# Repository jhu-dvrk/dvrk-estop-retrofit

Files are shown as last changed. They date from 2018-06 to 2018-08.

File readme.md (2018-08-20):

# dVRK E-stop Retrofit Kit

This retrofit kit converts the 4-pin and 5-pin E-stop connectors on old dVRK boxes to the newer 4-and-5-pin connectors.

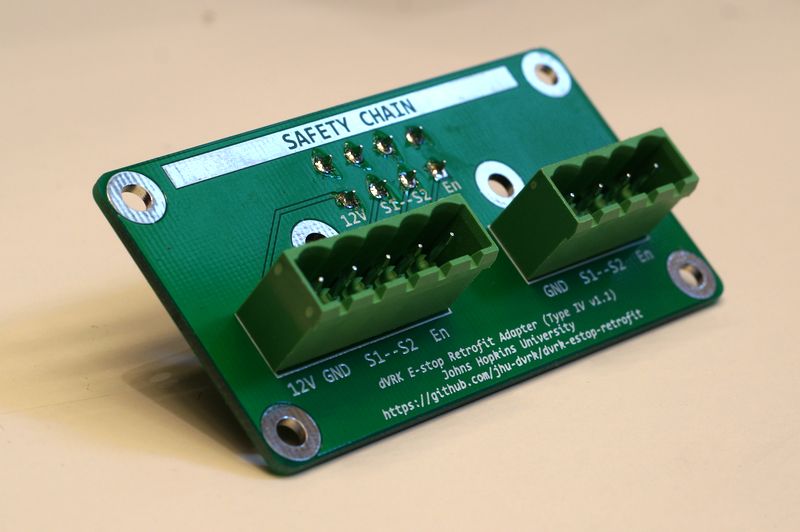
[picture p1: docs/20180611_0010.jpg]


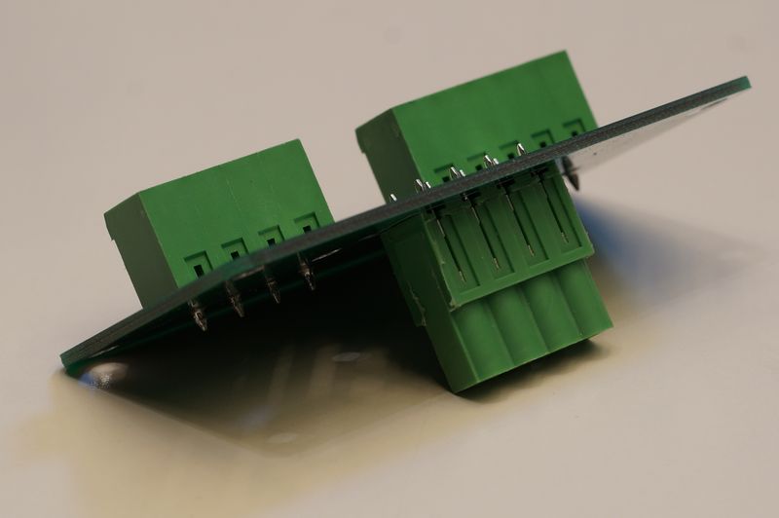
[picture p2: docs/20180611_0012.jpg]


**Why do I want the new 4-and-5-pin connectors?** The new connectors allow you to use the [JHU-style configurable serial connection](#making-the-cables), so you can quickly reconfigure the dVRK into two or more systems (e.g. one workstation for the MTMs, and another workstation for the PSMs) for different research needs. 

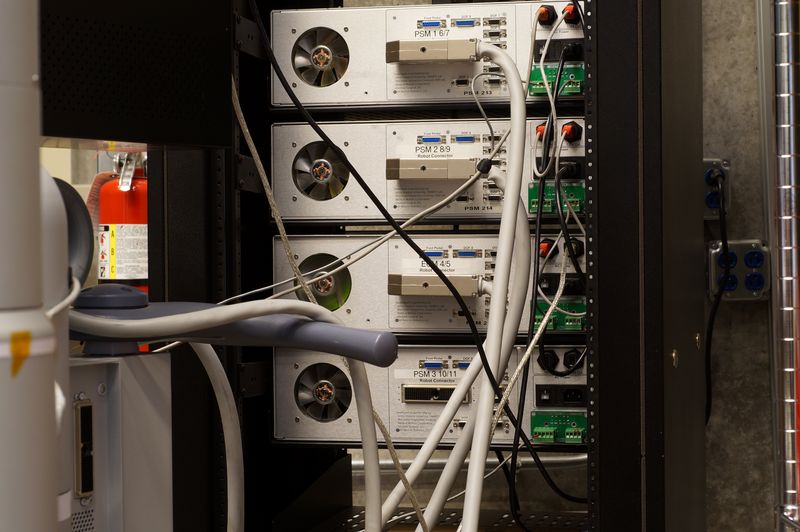
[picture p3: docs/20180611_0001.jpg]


dVRK at JHU with retrofit applied. Top three boxes are connected to one safety chain, and the bottom one is connected to another. PSM3 is used as an one-arm-only dVRK.

# Which "type" do I need?

Look at the back side (connector side) of the dVRK boxes. If you only see a green four-pin safety chain connector, you need `type iv`. If you only see a green five-pin connector, you need `type v`. Please check the visual identification guide below.

The "types" are silkscreened on the retrofit kit PCB. `type iv` has a four-pin PCB mount plug. `type v` has a five-pin plug.

## Four-pin green connector. You need `type iv`.

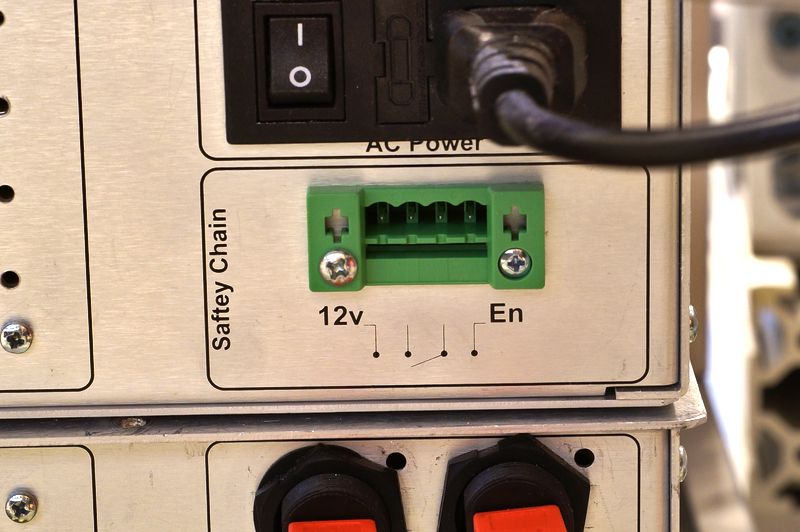
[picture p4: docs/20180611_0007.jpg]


## Five-pin green connector. You need `type v`.

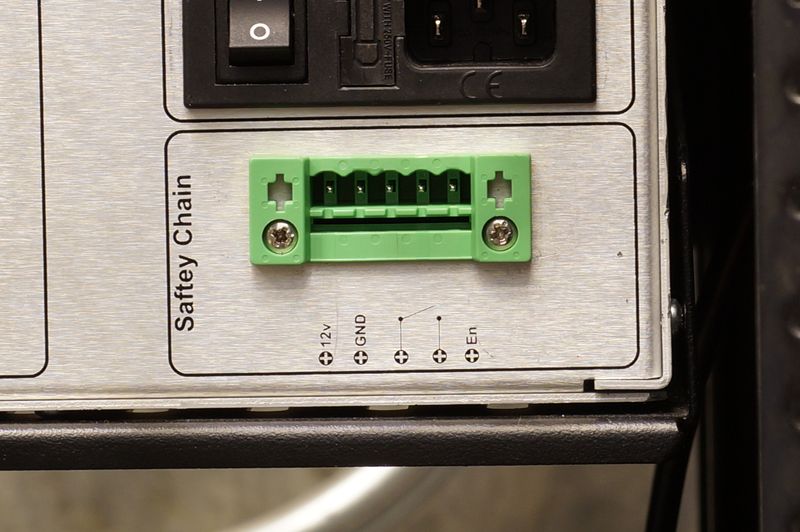
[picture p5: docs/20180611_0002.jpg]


##  Two five-pin connectors. Retrofit optional using `type v`.

If your dVRK boxes have two five-pin connectors, you can install `type v` as shown below.

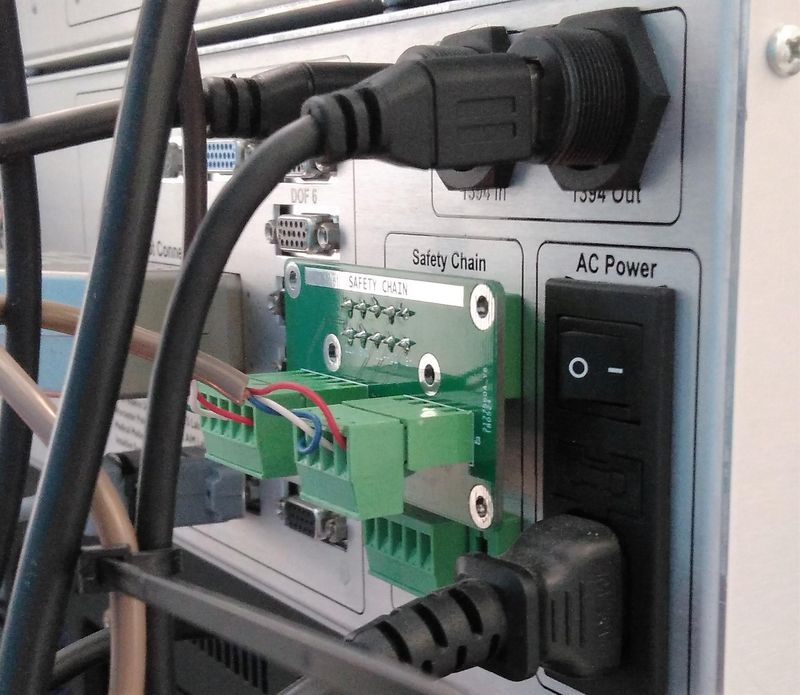
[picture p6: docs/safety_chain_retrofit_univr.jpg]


Alternatively, you can use the wiring documented [below](#making-the-cables) with your existing connectors, but ignore the extra `12V` pin.

## Four-pin and five-pin connectors. Retrofit not needed.

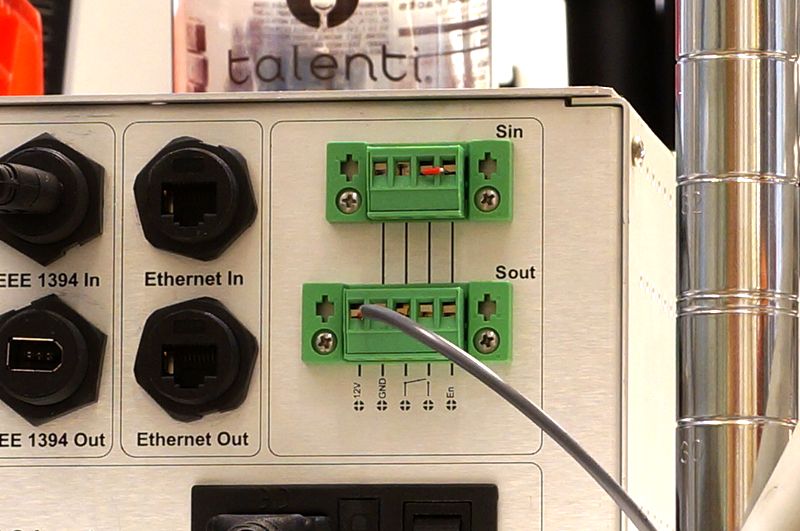
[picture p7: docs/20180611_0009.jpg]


If your dVRK boxes have these four-pin and five-pin connectors, you have the latest connector and you do not need this retrofit kit. Your system is probably already wired as recommeded [below](#making-the-cables).

# How to use

You should receive an assembled PCB with one screw terminal plug connector for each box. You will reuse the screw terminal plug connectors and the e-stop button that came with your boxes. The retrofit process at JHU took about half an hour for six boxes. 

## Making the cables

Please use the following diagram as a reference to make the cables.

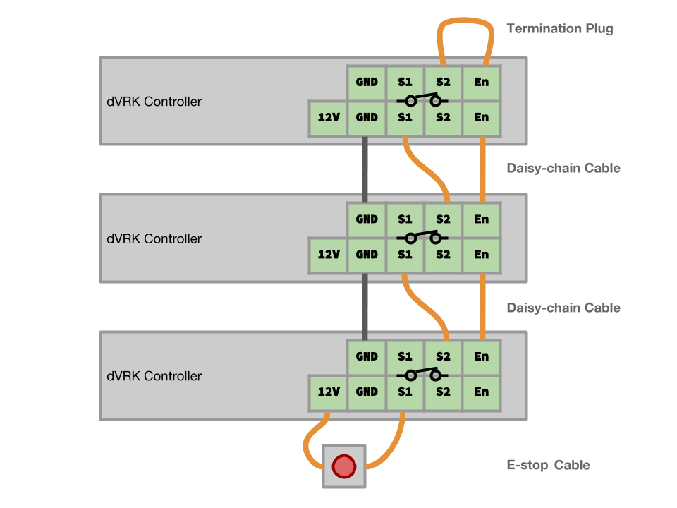
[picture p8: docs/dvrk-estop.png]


You can use any 3-wire (or more) cables to make the cables. The cable normally carries no more than a few milliamps of current. We strongly recommend using stranded wires, as solid wires tend to fracture under repeated flexing. We recommend using wire ferrules for aesthetics and strain relief, but inserting the bare stranded wires into the screw terminals is fine.

## Plugging it in

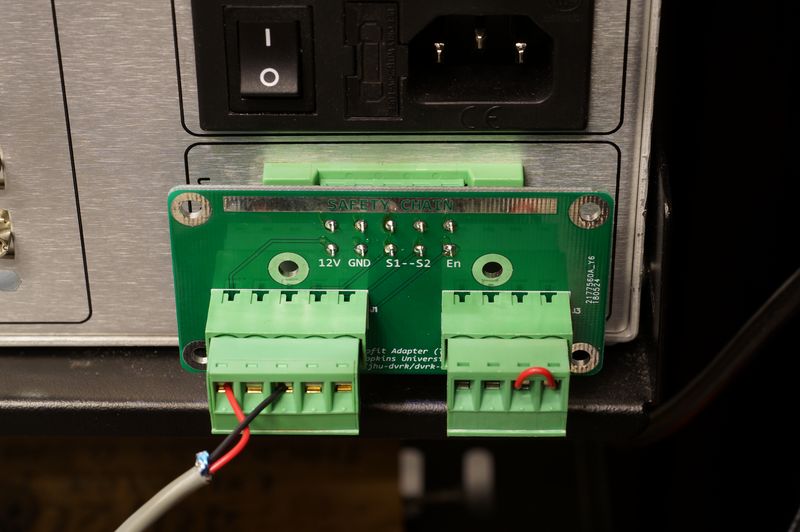
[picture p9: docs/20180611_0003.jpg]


If you are using the `type v`, you can directly plug the PCB assembly into the green connector behind the box, then plug the e-stop button, daisy-chain cables, and termination plugs into the PCB assembly. 

If you are using the `type iv`, you can directly plug the PCB assembly into the green connector behind the box if all boxes are sharing the same ground. Usually they are because their ground pin in the IEC connectors are connected at the power strip. If your e-stop already works, you probably have a working ground connection. 

The single four-pin e-stop connector does not have a ground pin. If you suspect that you are having a grounding problem, you can replace the screw in the panel-mount green receptacle with longer ones that will extend to the retrofit board. The screw holes on the retrofit PCB are all connected to the ground pins.

Once you connect all e-stop buttons, cables, and termination plugs, the e-stop should work. Happy dVRKing!

You can 3D print a shroud to make the board sit nicer on the back panel. If you do so, please share the model with us!

# Making your own boards/getting more connectors

Check releases of this repository for the latest gerber files for the PCB. You can upload it to your favorite PCB fab. If you only need a couple boards and you are located in the US, OSHPark is a good option.

The 5.08mm connectors are very standard and a lot of companies make them. If you are looking for more plugs so you can have multiple e-stop chains, any of [these](https://www.digikey.com/products/en/connectors-interconnects/terminal-blocks-headers-plugs-and-sockets/370?FV=1600018%2C1600006%2C1640056%2Cffe00172%2C2dc1f64%2C2dc1f65%2C2dc1f66%2C2dc1f67%2C2dc1f68%2C2dc1f6c%2C2dc1f6d&quantity=0&ColumnSort=0&page=1&pageSize=25) will do. [This
(4-pin)](https://www.digikey.com/product-detail/en/phoenix-contact/1776155/277-6223-ND/348998) and [this (5-pin)](https://www.digikey.com/product-detail/en/phoenix-contact/1776142/277-6473-ND/348997) are particularly nice because they have zip tie anchors.

The PCB mount plugs are hard to find. We used Wurth Elektronik 691307500004 and 691307500005.

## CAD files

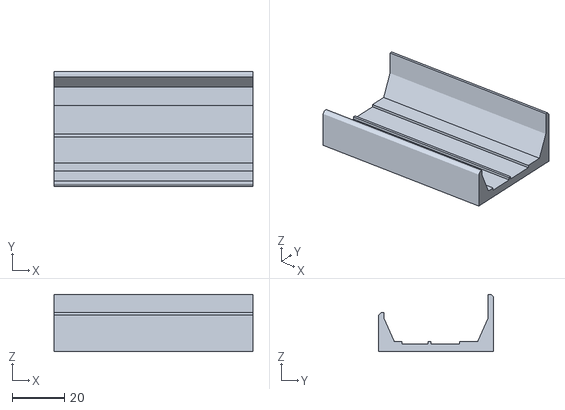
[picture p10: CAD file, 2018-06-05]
soldering-jig.stl
76.2 x 44.0 x 22.0

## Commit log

2018-04-25 made twentyfour
    [twentyfour.PcbDoc, twentyfour.PrjPCB, twentyfour.SchDoc]
2018-04-27 changed name
    [twentyfive.PcbDoc, twentyfive.PrjPCB, twentyfour.PcbDoc, twentyfour.PrjPCB]
2018-06-05 added soldering jig
    [soldering-jig.stl]
2018-06-20 Added cable to e-stop
2018-08-20 Added photo and updated text for case with two 5-pin connectors
